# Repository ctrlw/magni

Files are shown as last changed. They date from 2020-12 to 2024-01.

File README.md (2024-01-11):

# magni
Buy me a coffee (https://www.buymeacoffee.com/ctrlw)

Software for a simple video magnifier running on Raspberry Pi. The first video demonstrates magnification and colour inversion, the second reading out text.

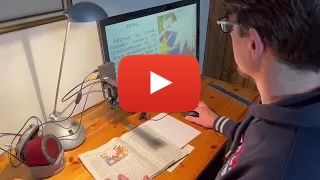
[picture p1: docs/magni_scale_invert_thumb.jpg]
Demo of video magnifier with magnification levels and colour inversion (https://youtu.be/32cXs6KolWk "DIY video magnifier demo scaling text and inverting colours")

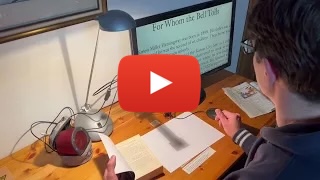
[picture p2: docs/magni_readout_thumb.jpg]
Demo of video magnifier reading out text from a book (https://youtu.be/zVkWfopQ86A "DIY video magnifier reading out text from a book")


## Description
This project aims to build a video magnifier based on Raspberry Pi and its camera. It can be used to see printed text or images at a larger scale, or to identify small parts like SMD electronics. The device has to be connected to a monitor which displays the magnified image from the camera. The user can step through predefined scale factors with a button or the Enter key, and step through different colour modes (like colour-inversion) with a second button or the "/" key. There's also basic support for reading out text (supports English, Spanish, French, German or Italian).

After the initial setup, the device works fully offline and does not need an internet connection.

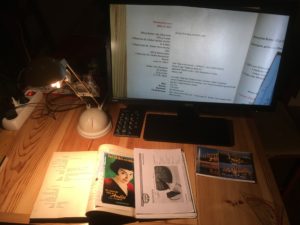
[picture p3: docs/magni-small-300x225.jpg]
Magnifier with low magnification

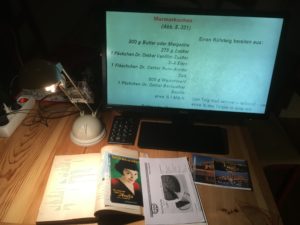
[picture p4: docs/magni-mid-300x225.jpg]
Magnifier with medium magnification

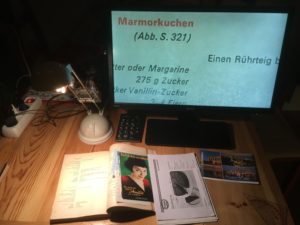
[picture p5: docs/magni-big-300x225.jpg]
Magnifier with high magnification


## Usage
The device boots directly into (slightly magnified) fullscreen camera view, which can take a minute depending on the Raspberry Pi model and SD card. It's important that the monitor is powered on at the same time as the Raspberry Pi or before, otherwise we may not get the full resolution. This can be achieved e.g. using a switchable socket or powering the Raspberry Pi directly from the monitor. 

The script supports multiple input sources:
* Mouse
  * Left button: switch to next magnification level (from smaller to bigger, then jump back to first)
  * Right button: switch between regular view and colour inversion / colour modes
  * Middle button: read out the text on the screen, stop it if already processing
  * Movement: no impact, the mouse is only used for its buttons. The recommendation is to prevent the mouse from accidental slipping, e.g. by sticking rubber bumpers on the bottom
* Keyboard (also supports a small numeric keyboard for the main features)
  * Enter: switch to next magnification level
  * /: switch between regular view and colour inversion / colour modes
  * r: read out the text on the screen, stop it if already processing
  * z: zoom in
  * Z: zoom out
  * a: autofocus (only with v3 camera, also happens automatically on each magnification change)
  * f: focus a bit closer
  * F: focus a bit further away
  * b: increase brightness
  * B: reduce brightness
  * c: increase contrast
  * C: reduce contrast
  * h: increase sharpness
  * H: reduce sharpness
  * t: increase saturation
  * T: reduce saturation
  * s: save the current preview as an image, name is the current timestamp
  * 1-0: set magnification level to specific value between 1 and 10
  * Esc or q: quit
* Push buttons via GPIO, one to iterate to the next scaling factor and one to switch between colour inversion / colour modes

## Hardware
To build the magnifier, you need at least the following
* Raspberry Pi
  * Any model you have will do (except Pi Pico), but if you're going to buy one I'd recommend the Pi 3 or Zero 2 W
  * Raspberry Pi Zeros are nice for their size, but need specific cables/adapters for camera and USB
  * Raspberry Pi 4 and 5 need specific cables/adapters and may also need cooling. They are overkill for the magnification task but could be faster for Text-To-Speech (reading out content)
* Raspberry Pi camera
  * Strongly recommended is an official Raspberry Pi camera v2 or v3, due to better image quality and flexible focus compared to the original 5MP ones. The v3 has autofocus which can be handy when supporting different distances to surface (e.g. when mounted on a flexible arm). However, the autofocus is not always accurate, so a v2 camera that is tuned to the right distance can be the better choice if you have a fixed distance to the surface. The high quality camera with additional lenses is not needed. The v3 version with Wide angle could be useful for close distances but has aberrations in the corners, so the regular v3 is probably the better choice.
* Raspberry Pi camera cable
  * only if the standard 15cm cable is too short or you need the smaller cable for Raspberry Pi Zero
* USB charger. For higher specced Raspberry Pi models (3 upwards) the official chargers are recommended due to better power stability
* Micro SD card (>= 4GB)
* HDMI monitor + cable. Some Raspberry Pi models work with analog TVs as well, but this hasn't been tested. A 22-24" FullHD monitor is good and can be found for 100
* Some input device. The easiest way is a USB (cable) mouse just for the buttons, but a numerical keyboard is also possible, or you can even solder physical push buttons to the GPIO
* Material for the mount

## Mount
The setup can be built in different ways, so let your creativity flow. Here are some examples:
* [Lamp setup](docs/magni-lamp-mount.md) (basic and simple)
* [Flexible arm](docs/magni-flexible-arm-mount.md) with one push-button
* [Box setup](docs/magni-box-mount.md) with 2 push-buttons
* [3d print for Pi Zero](docs/magni-3d-zero.md)

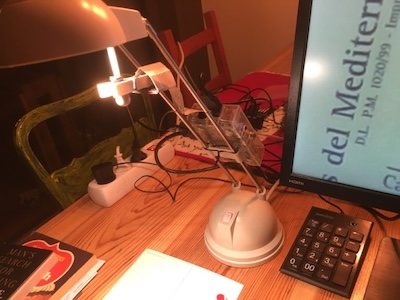
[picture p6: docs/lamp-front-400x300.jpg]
Simple lamp setup

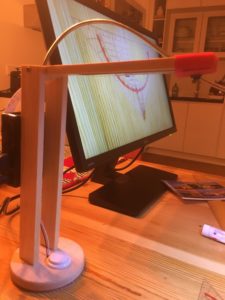
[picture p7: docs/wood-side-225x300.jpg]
Flexible wood arm

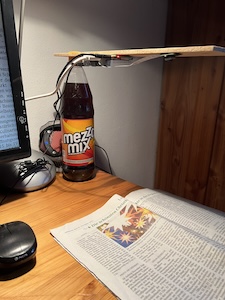
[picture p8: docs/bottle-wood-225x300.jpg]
Board on bottle

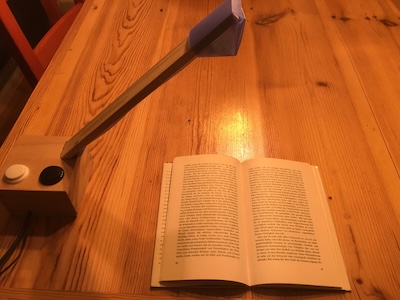
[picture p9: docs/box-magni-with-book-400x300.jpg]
Box setup with push buttons

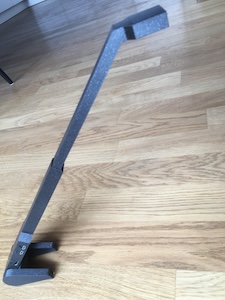
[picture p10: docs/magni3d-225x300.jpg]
3d print for Pi Zero

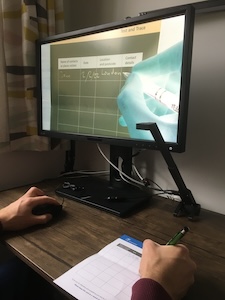
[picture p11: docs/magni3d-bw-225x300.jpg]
3d print for Pi Zero b/w

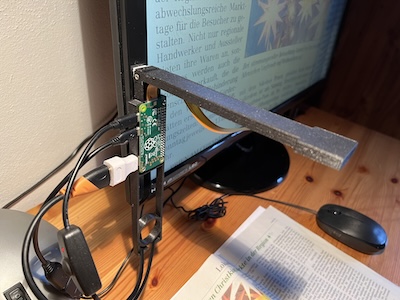
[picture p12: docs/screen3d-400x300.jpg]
3d print on monitor


A slightly more in-depth description of the first 2 hardware setups is given at http://www.fhack.org/2018/12/19/raspberry-pi-video-magnifier-2018/

If you use the optional push buttons instead of a USB mouse or numerical keyboard, the script expects them at GPIO 4 (physical 7) for the scale button and GPIO 18 (physical 12) for the colour button, using BCM numbering (4 being the 4th pin on the left, 18 being the 6th pin on the right of the GPIO). Each button needs to be connected with GND, e.g. at pins 9 and 14.
While physical buttons are nice, this involves soldering and they may be susceptible to electro-magnetic noise (e.g. getting triggered from switching some device on/off, or even from static charges from my Ikea Markus chair).

## Setup
**2021's Raspberry Pi OS "Bullseye" introduced some incompatible changes for the camera module. The following steps assume you use the latest OS, but the older "Bullseye" OS is still available as "Legacy OS" and allows to set the camera as Legacy camera in raspi-config (Interface options -> (Legacy) Camera -> Enable). The python script should work with both but the setup for legacy camera support is slightly different and can be found below.**
* Download [Raspberry Pi OS **Lite**](https://www.raspberrypi.org/software/operating-systems/) and install on SD card, e.g. with Raspberry Pi Imager. The 32 bit version is usually fine
* [Connect camera](https://www.raspberrypi.com/documentation/accessories/camera.html#connecting-the-camera)
* Login with default user “pi”, password “raspberry” (if on desktop, open a terminal). Using the default credentials is not secure, so change it if you will connect the device to the internet or have it accessible to strangers
* Run `sudo raspi-config`
  * System options -> Boot / Autologin -> Console Autologin
  * System options -> Wireless LAN (if you want to connect from another computer by wifi)
  * Interface options -> SSH -> Enable (only if you want to connect from another computer)
  * Finish and reboot (<Yes> or `sudo reboot`)
* Run the following commands in the terminal:
```
sudo apt update && sudo apt -y upgrade
sudo apt install -y python3-picamera2 python3-gpiozero python3-evdev python3-opencv
wget https://github.com/ctrlw/magni/raw/master/magni.py
chmod +x magni.py
echo "clear" >> .bashrc
echo "./magni.py" >> .bashrc
```
* To have a lower-quality fallback in case the monitor / TV is switched on *after* the magnifier, edit /boot/config.txt:
 `sudo nano /boot/config.txt`. This doesn't seem supported in the latest OS anymore.
  * Move to the line `#hdmi_force_hotplug=1` and delete the first character (#)
  * Leave nano with Ctrl-x, press “y” to save and enter to update the given file

* To hide the messages during startup, edit /boot/cmdline.txt:
`sudo nano /boot/cmdline.txt`
  * Append the following at the end of the line and save the file:
` logo.nologo quiet splash`
  * Leave nano with Ctrl-x, press “y” to save and enter to update the given file

### Legacy OS
The setup is the same as above with the following exceptions:
* In `sudo raspi-config` also enable Legacy camera support: Interface options -> Legacy Camera -> Yes
* When installing python libraries with apt, install `python3-picamera` instead of `python3-picamera2`, and you can skip `python3-opencv` as colour inversion is supported out of the box but not the colour modes
* For Readout (see below) use `bullseye` instead of `bookworm`. However, the area being read differs from the visible preview.
* You can use `libcamera-still` and `raspistill` instead of `libcamera-hello`

If you enable Legacy camera support, v3 cameras are not supported (at all, not just the autofocus!). The main advantage with legacy camera is the faster colour inversion, which can be otherwise slow on older models like the original Pi Zero or the Raspberry Pi models before the Pi 3. However, other colour modes like yellow on blue are only supported with the newer OS and needs opencv installed.

### Support reading out the visible text (OCR + TTS)
This feature is a very basic approach to read out text that is visible on the screen. It gets triggered when pressing the middle button of the mouse or "r" on an attached keyboard. Pressing the key again while it's still processing stops the background process.

All processing happens on the device itself (no internet needed), so better Raspberry Pi models will compute results faster. This feature is very sensitive to image quality and correct alignment, so ensuring good light, clear focus and horizontal text is necessary for reasonable results.

To make this work there are some extra dependencies. For Text to speech (TTS) we use pico2wave which is not included in the Raspberry Pi OS sources, so we have to add upstream Debian sources.
```
echo "deb [arch=armhf, trusted=yes] http://deb.debian.org/debian bookworm main contrib non-free" | sudo tee -a /etc/apt/sources.list
sudo apt update && sudo apt install -y tesseract-ocr libttspico-utils
wget https://github.com/ctrlw/magni/raw/master/plop.wav
```
The current OS (in late 2023) is based on bookworm. If you're on a different version you may have to adapt the first line accordingly, e.g. replace `bookworm` with `bullseye` if you're on the Legacy OS.

For other languages than English you need to install the related language packs. The used TTS package only supports 6 voices (en-GB, en-US, de-DE, es-ES, fr-FR, it-IT), so you can install all necessary OCR languages with
```
sudo apt install -y tesseract-ocr-deu tesseract-ocr-spa tesseract-ocr-fra tesseract-ocr-ita
```
and then update the language in magni.py, e.g.:
```
OCR_LANG = 'deu'   # Tesseract's character recognition: eng, deu, spa, fra, ita
TTS_LANG = 'de-DE' # Pico's Text to Speech: en-GB, en-US, de-DE, es-ES, fr-FR, it-IT
```

Sound may come through HDMI if you have a screen with speakers, or through the headphone jack of some models like the Pi 3. This can be changed in `sudo raspi-config` under System options -> Audio -> Headphones / HDMI. You can test that sound works running the built-in `speaker-test`.
There seems to be an issue where [audio via HDMI doesn't work as expected](https://forums.raspberrypi.com/viewtopic.php?t=351718). As a workaround you can force `aplay` to use HDMI output by uncommenting the second AUDIO line in the script to show `AUDIO = 'aplay -D sysdefault:CARD=vc4hdmi'` (if `speaker-test -D sysdefault:CARD=vc4hdmi` works).

### Support hard shut-down
This step allows to simply unplug the Raspberry Pi without possible damage to the SD card. This should be the last step in the setup, as the system will be made read-only (but it can be undone if needed).

Run `sudo raspi-config`
* Performance options -> Overlay File System
  * Enable overlay file system: Yes
  * Write-protect boot partition: Yes
  * Reboot? Yes

Now you can still create and modify files locally, but they will not be written to the SD card and disappear on the next reboot.
If you want to make the system writable again, you can do it in 2 steps with raspi-config:
* Disable the Overlay File System, so you can write to the file-system
* If you also want to modify the boot partition, you have to do it in a second step after rebooting

## Camera focus
**If you use the camera v3 with its autofocus you can skip this step as it doesn't need manual setup.**

When everything is in place, adjust the focus till a letter under the camera looks sharp. Then try a book and maybe adjust. Not all objects are flat. The  Raspberry Pi camera v2 usually comes with a white ring tool to easily adjust focus. On the older camera model or cheap alternatives, the lens may be glued and can still be adapted, but you risk breaking the camera.

You can do this with the magni.py script, or run `libcamera-hello --rotation 180 -t 0`:
* If you see the current camera view and it's at the same angle that you have from above (e.g. it’s not upside down), you’re good, otherwise try different values for rotation (0, 180) and adapt the ROTATION value in magni.py accordingly
* If the image is blurry you should adjust the focus, simply turning the lens with the plastic “wheel” that comes with the Pi camera v2
* Use Ctrl-c to get out of libcamera-hello (or Esc to leave the magni script)

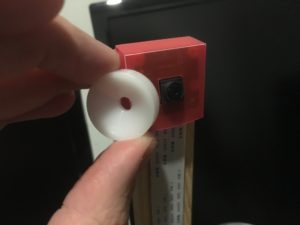
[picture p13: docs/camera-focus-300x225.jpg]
Adjust camera focus


## Modifications
You can easily adapt magni.py to your own setup and needs:
* `SCALE_FACTORS`: Modify this line to specify the scale factors
* `PIN_NUMBER_SCALE`: Set the (BCM) GPIO pin number where you connect the optional scale push-button
* `PIN_NUMBER_COLOR`: Set the (BCM) GPIO pin number where you connect the optional colour-mode push-button
* `ROTATION`: Change the value to the camera rotation in your setup if the camera is not placed behind the object (supports 0, 180; picamera on legacy OS also allowed 90 and 270 but this isn't the case on newer OS versions)
* `DISTANCE_TO_SURFACE_CM`: Can be overridden for v3 camera to fix the focus at a specific distance, default is autofocus
* `AUDIO`: Can be modified to force audio via HDMI if `raspi-config` isn't enough, just uncomment the respective line
* `BRIGHTNESS`: Can be modified to start with different brightness, values between -1.0 and 1.0
* `CONTRAST`: Can be modified to start with different contrast, values between 0.0 and 32.0
* `SHARPNESS`: Can be modified to start with different sharpness, values between 0.0 and 16.0
* `SATURATION`: Can be modified to start with different saturation, values between 0.0 and 32.0
* `COLOR_MODES`: Can be modified to change the list of supported colour modes to step through

## Limitations
* The monitor has to be switched on before or at the same time as the Raspberry Pi
* Magnification is done in software, so scale factors of 10 and above tend to be noisy
* On older cameras the camera focus is fixed, so it cannot adapt to objects that are much closer or further away. Pi camera v3 supports autofocus but it's often not that accurate
* It may take a minute from power on till the picture is shown (depending on model and SD card)
* The readout feature is very basic and mostly a proof of concept

## Alternatives
This is a fun project, but also consider these alternatives to building your own video magnifier
* Smartphones and tablets usually come with a magnification option, e.g. the built-in [Magnifier on iOS](https://support.apple.com/en-us/HT209517) and [Google's Magnifier on Android](https://play.google.com/store/apps/details?id=com.google.android.apps.accessibility.magnifier)
* A mounted magnifying glass as they are used in nail salons
* Professional video magnifiers are optimised for low vision users with varying needs and conditions. While they cost in the thousands, it's often possible to find them much cheaper used, e.g. on Ebay. Depending on your location, health insurance providers or organisations for the Blind may also have special offers or even provide support for free
* Others have come up with similar DIY solutions which may be better suited, e.g.
  * [Precision zoom on Raspberry Pi](https://www.instructables.com/Raspberry-Pi-Zero-HDMIWiFi-Soldering-Microscope/)
  * [Borescope camera and laptop](https://www.instructables.com/Reading-Aid-for-the-Partially-Sighted/)
  * [USB camera and laptop](https://github.com/mikeh69/EVidMag)

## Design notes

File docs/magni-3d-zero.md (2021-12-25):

# Small 3d printed video magnifier
Simple and compact 3d-printed setup that is good enough for books and also works for the occasional letter. For Raspberry Pi Zero with 30cm ribbon cable. Uses mouse buttons for input.

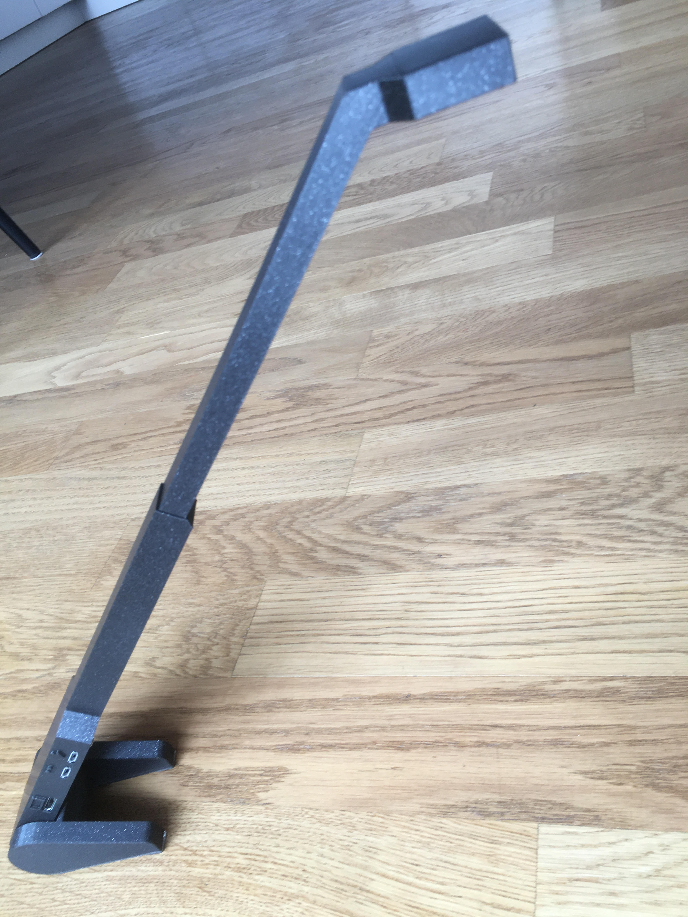
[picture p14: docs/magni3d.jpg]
Assembled magni


## Ingredients
* HDMI monitor (22-24 inch is a good size)
* Raspberry Pi Zero
* Raspberry Pi Camera v2
* 30cm camera ribbon cable for Raspberry Pi Zero
* USB Mouse (as input device)
* Micro USB to USB adapter (for the mouse)
* 8 screws (2mm diameter, 10mm length)
* 1 M16 connecting nut (16mm screw diameter, 24mm outer diameter, 50mm length) as weight
* HDMI cable with one side mini HDMI, other normal size HDMI
* Micro USB charger
* (optional) rubber stickers to stick under the mouse, to avoid it moving (as we only use the buttons)

## 3d printed parts
Print the following parts on a 3d printer (tested with PLA on a Prusa Mini):
* [Body](../stl/zero-wide-body7.stl)
* [Cover for body](../stl/zero-wide-bottom7.stl)
* [Camera arm](../stl/zero-wide-arm3.stl)
* [Cover for arm](../stl/zero-wide-arm3-inner.stl)
* [Foot](../stl/zero-wide-foot7.stl)
* [Other Foot (same file, but you have to flip it before printing)](../stl/zero-wide-foot7.stl)

## Building
* Attach camera cable to camera, pass the cable through the camera arm and screw the cover onto the camera
* Stick camera arm into body
* Attach other end of the camera cable to Raspberry Pi
* Screw the body cover onto Raspberry Pi
* Insert M16 nut into the cavity at the end of the body
* Stick feet on both sides of the M16 nut so the device is at a 45 degrees angle
* Connect HDMI cable to the monitor
* Connect mouse and micro USB adapter to the center micro USB port
* Connect micro USB charger to the other micro USB port

## Usage
One mouse button iterates through the pre-defined magnification factors, the other switches between normal and inverted colour mode.
Smaller items like books can be moved under the device. For bigger items like newspapers the device has to be moved on top of the paper which is less convenient.

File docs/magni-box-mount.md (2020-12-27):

# Box mount video magnifier
This setup uses a square box with a diagonal camera arm. Box and arm can be laser-cut, while you may want to 3d-print the camera enclosure or build it from plastic. If you position the magnifier on the side and not behind the object, you also have to adapt the ROTATION in the magni.py script. Image quality is worse when positioned sideways (with rotation 90 or 270).

This is more of a prototype that someone might want to expand on.

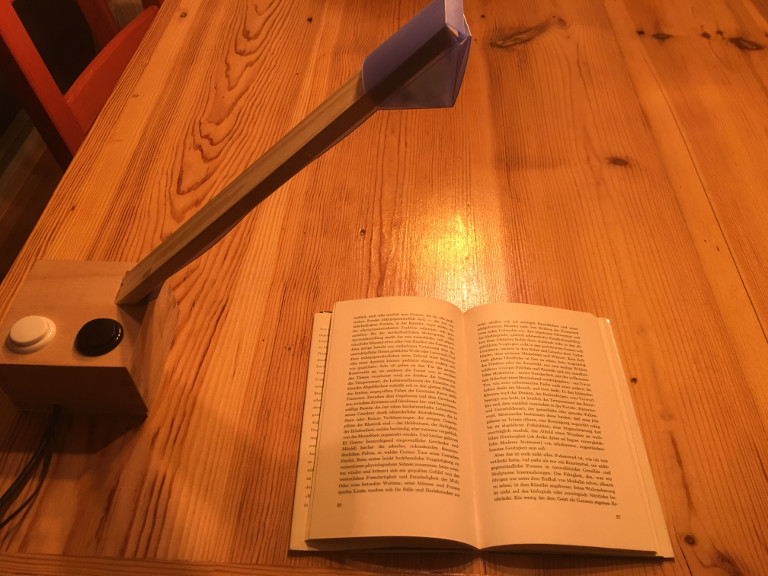
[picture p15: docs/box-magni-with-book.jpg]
Magni sideways


## Ingredients
* 2 Push-buttons (3cm diameter) and cables (like this [arcade set](https://www.amazon.de/dp/B06XDG6PC1))
* Wood glue
* ~A3 sized ply wood (4mm thick, laser-cuttable)
* Access to a laser-cutter
* LED lamp (optional, not shown here)

## Building
Cut the wood according to this [SVG for laser-cutter box](box-magni-laser-4mm.svg). Red lines should be cut, green just marked and blue can be carved for cables to add an LED light. The design hasn't taken into account that laser cuts also have a width, so the parts will not be stable just by combining them, but the wood needs to be glued.
For illustration purpose here's an older [pdf for laser-cutter box](box-magni-laser-a4.pdf), which does not contain the camera arm and may not be adapted to 4mm wood.

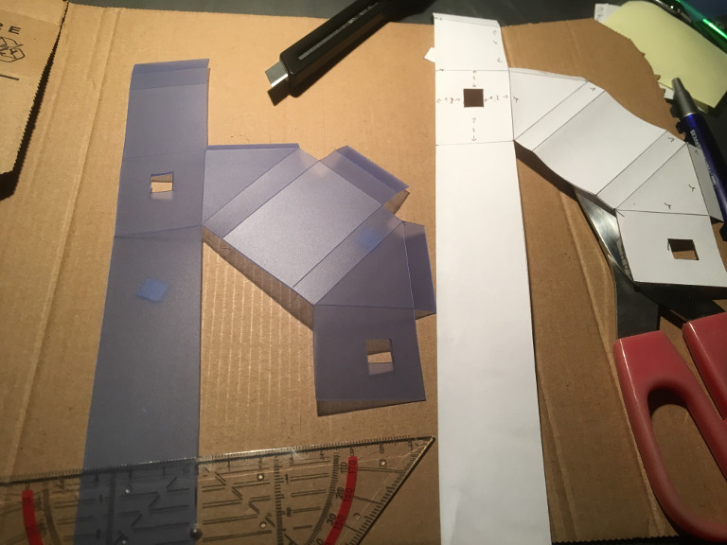
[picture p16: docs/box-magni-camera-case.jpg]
Camera enclosing


## Usage
One push-button steps through magnification levels, the other toggles colour inversion.

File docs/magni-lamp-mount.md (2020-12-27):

# Lamp mount video magnifier
This is the most basic setup. 

## Ingredients
* Raspberry Pi case (had a Raspberry Pi 1 with official case)
* Lamp (had a basic halogen lamp from the hardware store)
* Numeric keypad
* Wooden peg with a bit of rubber gum inside
* Twist tie (to attach the case to the lamp)
* Cardboard to “protect” the camera

## Building
There’s really nothing to it. Very simple to “build”. Not exactly stable.

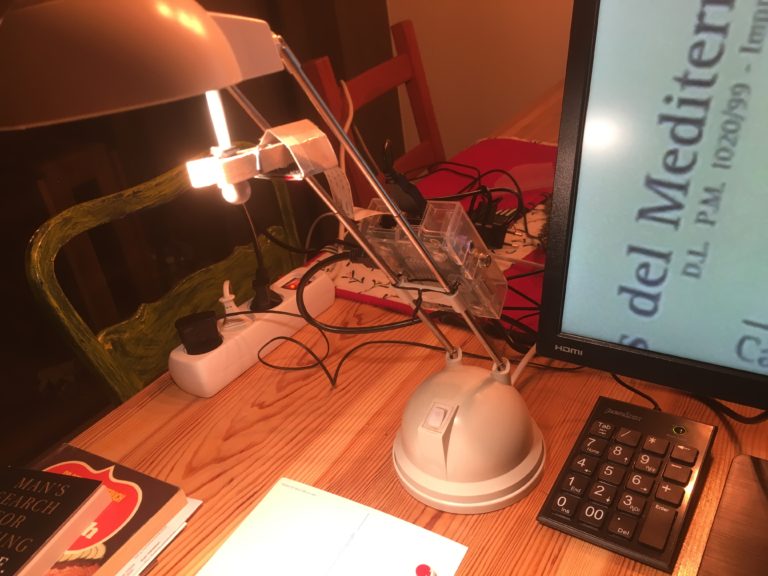
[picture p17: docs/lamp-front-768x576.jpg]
Magni lamp setup front

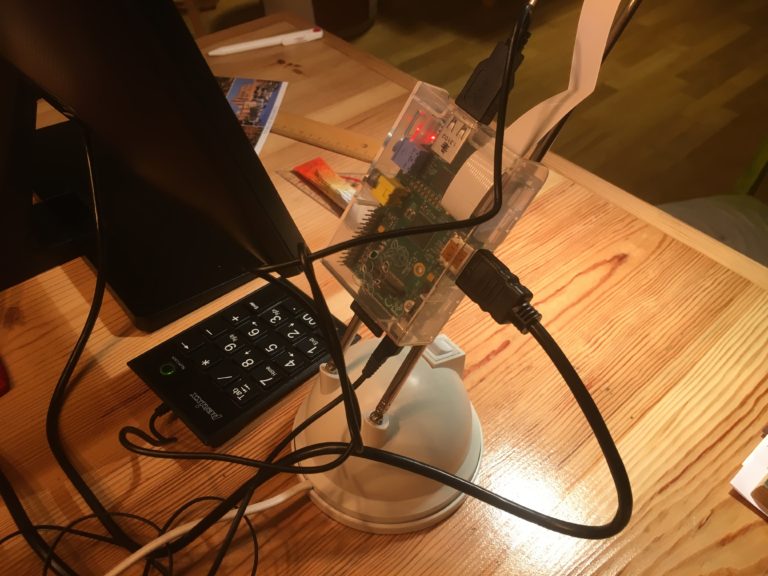
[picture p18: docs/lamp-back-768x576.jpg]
Magni lamp setup back


## Usage
Pressing a digit on the numeric keypad switches magnification to that factor (except for too small values, i.e. "1" normally does nothing). Pressing the Enter key switches to next preset magnification level. Pressing “/” inverts colours (some people are better reading white text on black background). This is not exclusive to this build, of course the keypad can also be attached to other versions.

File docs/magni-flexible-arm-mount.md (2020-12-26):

# Flexible arm magnifier
This design is more (wood-) work. The arm is flexible, so the device can be folded for transport. The single button makes it easy to use, and you can move the arm up and down to see more / less (e.g. slightly move upwards for a big newspaper). Sizes can be adapted for its typical use case, e.g. for regular newspaper reading a bigger stand may be needed. 

Flexible arm magnifier setup

## Ingredients
* Raspberry Pi case with holes for GPIO cables
* USB LED lamp
* Wood (3cm x 1cm, 2 * 25cm, 1 * 20cm)
* Wooden wheel (10cm diameter, 1.5cm thick or more)
* Screws (4 * 2 cm to fix arm and Raspberry Pi, 2 * 4cm to fix bottom)
* Flex band 30cm for Raspberry Pi camera (or 50 cm if you make it bigger)
* Plastic to fold the camera case
* 2 jumper cables, 1 resistor (used 1k Ohm)
* 1 push button (3cm, taken from arcade joystick set)
* Rubber to keep it in place and protect push button electronics
* Tools: saw (Japan saws are great!), 2-3mm drill for pre-drilling the screws, 3cm drill for drilling the button hole, screwdriver, soldering equipment, cardboard cutter, glue

## Build
Below is a kind of step-by-step photo story. The screws for the case are about 15cm above the top of the base.

The jumper cables are attached to GPIO 7 and 9, i.e. the 4th pin on the left side and the neighbouring GND. I had to bend the push button connectors and break off one of its plastic pieces. Also cut one side of the jumper cables to solder to the button / resistor.

For the push-button I mostly followed https://raspberrypihq.com/use-a-push-button-with-raspberry-pi-gpio, and avoiding multiple click events with bounce time was a helpful addition from https://www.raspberrypi.org/forums/viewtopic.php?t=146369

The “case” for the camera is cut and glued from plastic and about 3cm x 3cm, with a height of 1.3cm, basically the wood plus about 3mm. The camera lens watches through an 8mm square. You can also 3d-print the [camera case STL](./magnicam.stl)

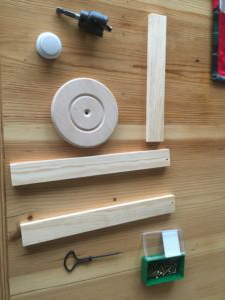
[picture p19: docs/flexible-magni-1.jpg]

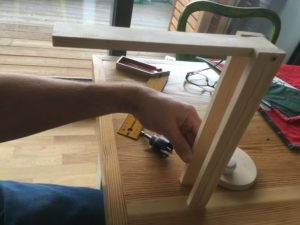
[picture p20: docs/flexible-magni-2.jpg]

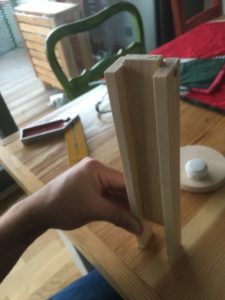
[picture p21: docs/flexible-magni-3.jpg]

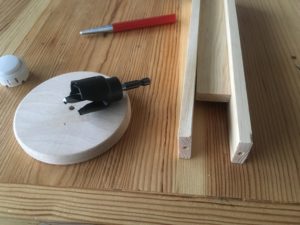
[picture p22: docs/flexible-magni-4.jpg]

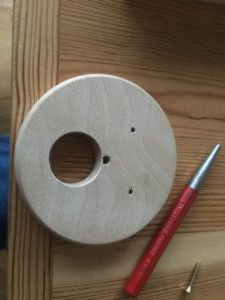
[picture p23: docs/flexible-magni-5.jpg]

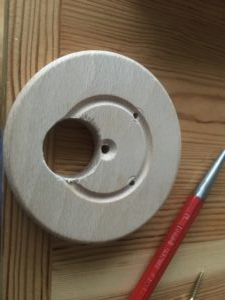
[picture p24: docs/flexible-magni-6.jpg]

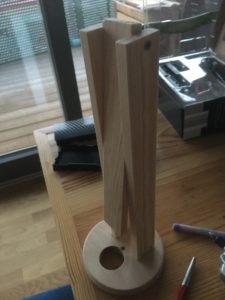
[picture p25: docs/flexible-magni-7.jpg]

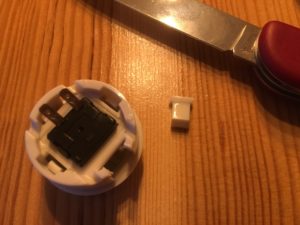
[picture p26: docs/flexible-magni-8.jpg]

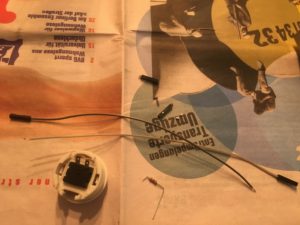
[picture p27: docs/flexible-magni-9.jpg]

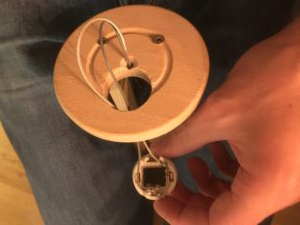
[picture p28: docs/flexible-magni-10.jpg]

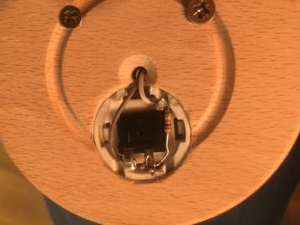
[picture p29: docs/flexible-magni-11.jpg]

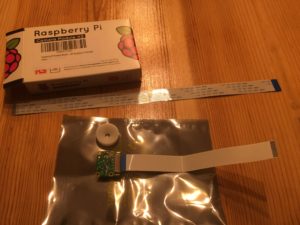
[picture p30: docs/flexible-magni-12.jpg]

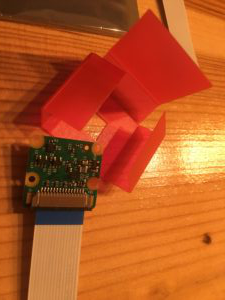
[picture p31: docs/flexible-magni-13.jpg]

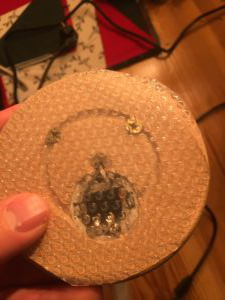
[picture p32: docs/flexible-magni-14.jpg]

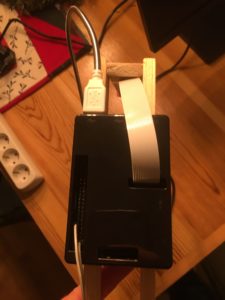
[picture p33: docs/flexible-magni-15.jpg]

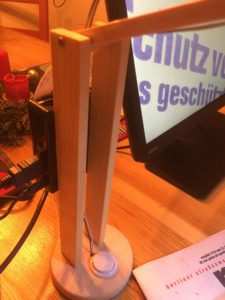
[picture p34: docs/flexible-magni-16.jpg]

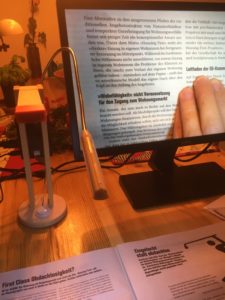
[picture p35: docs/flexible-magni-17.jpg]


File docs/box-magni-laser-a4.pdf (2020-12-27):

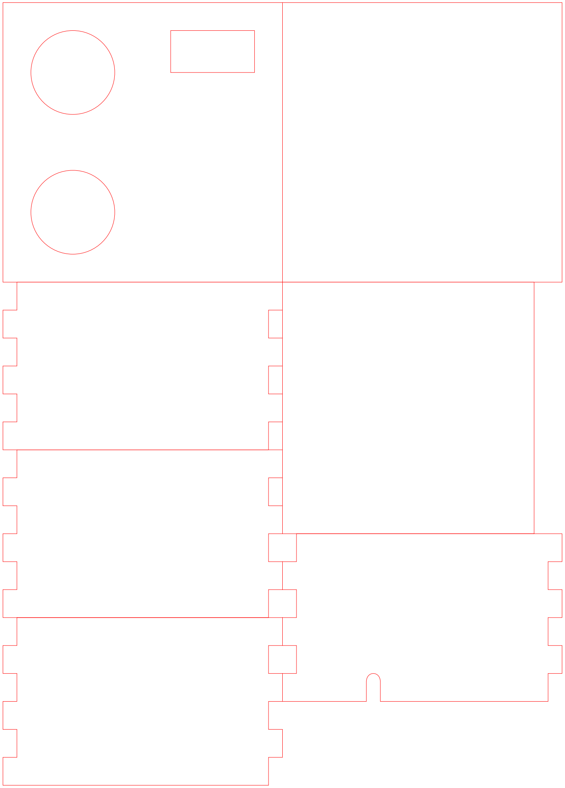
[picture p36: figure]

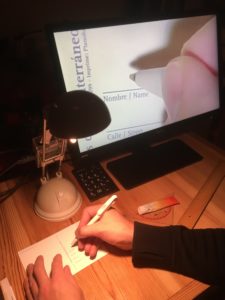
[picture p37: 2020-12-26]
docs/form-225x300.jpg

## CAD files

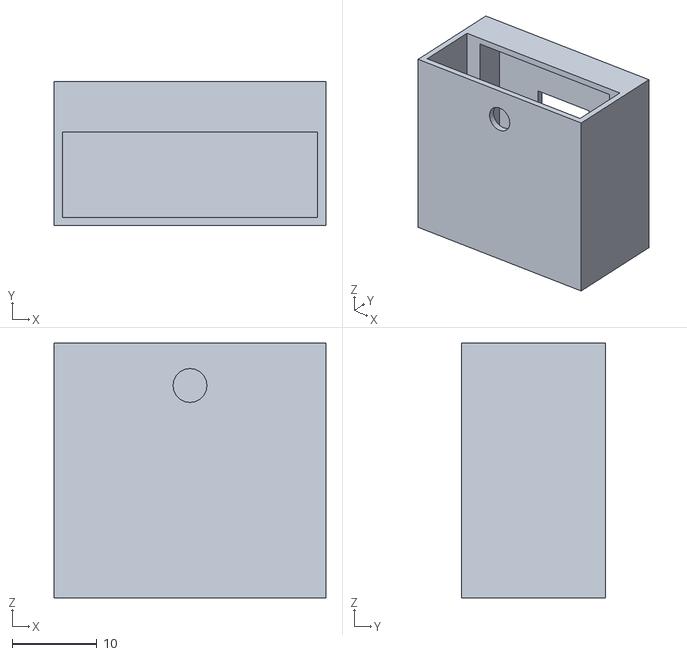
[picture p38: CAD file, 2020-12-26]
docs/magnicam.stl
32.0 x 17.0 x 30.0

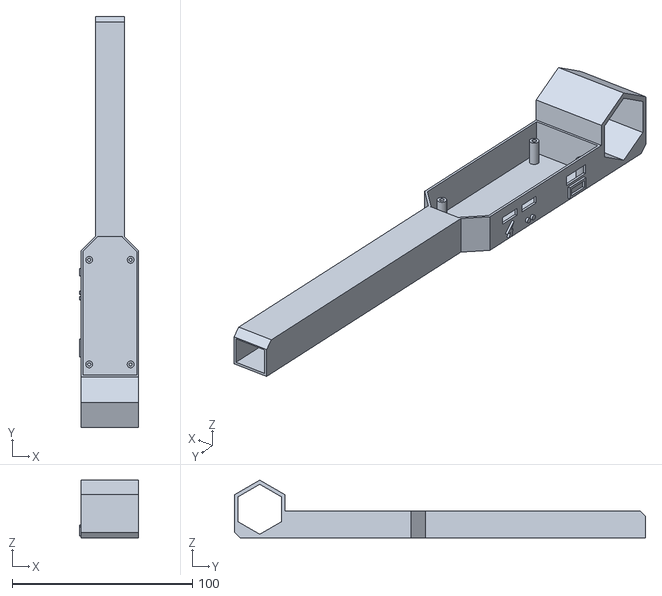
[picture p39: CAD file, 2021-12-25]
stl/zero-wide-body7.stl
33.0 x 228.0 x 32.0

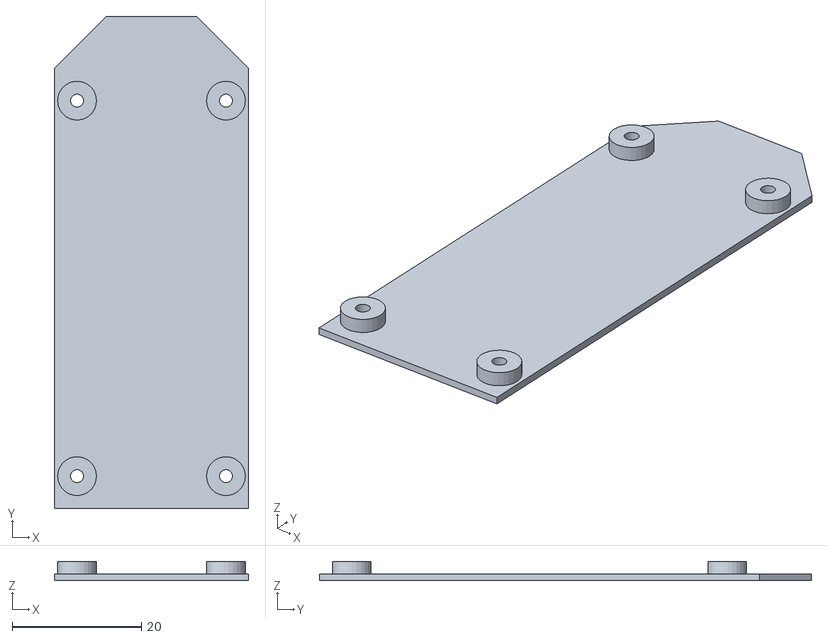
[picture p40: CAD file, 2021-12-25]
stl/zero-wide-bottom7.stl
30.0 x 76.0 x 3.00

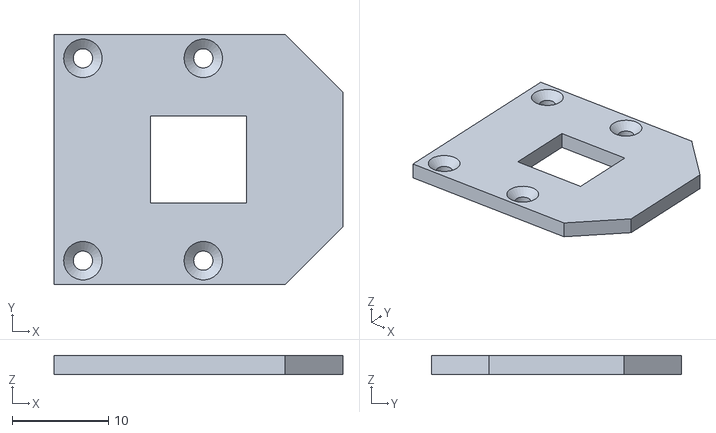
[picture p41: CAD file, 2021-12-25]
stl/zero-wide-arm3-inner.stl
30.0 x 26.0 x 2.00

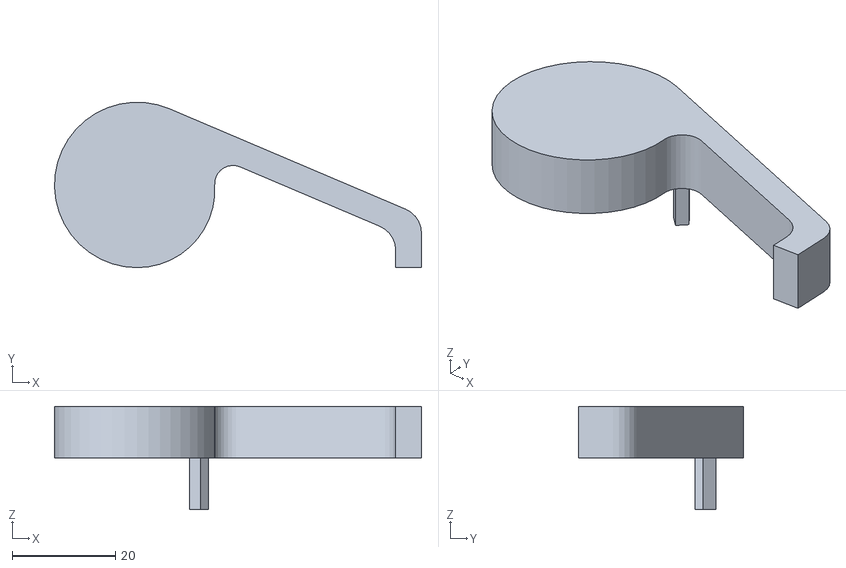
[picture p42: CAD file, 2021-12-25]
stl/zero-wide-foot7.stl
71.0 x 32.0 x 20.0

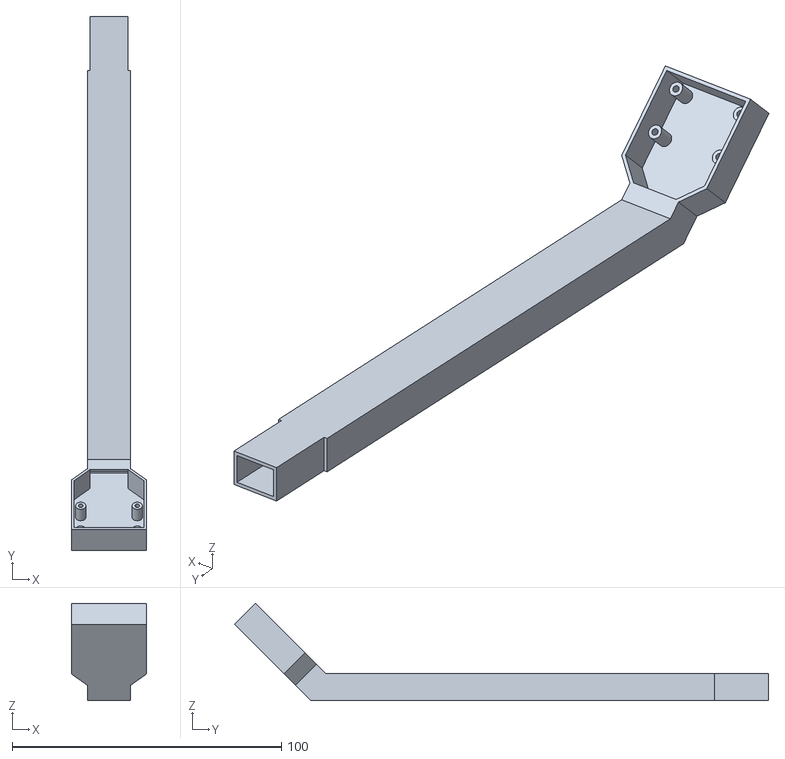
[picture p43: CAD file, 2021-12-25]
stl/zero-wide-arm3.stl
28.0 x 198.3 x 36.1

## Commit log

2019-03-15 fixed pin name
2020-12-25 Updated README.md for Raspberry Pi OS and PiCamera changes
2020-12-26 Add 2 build setups to documentation (lamp and flexible arm)
    [magnicam.stl]
2020-12-27 Description for 3rd housing with laser-cut box
2021-12-25 Add steps for new Raspberry Pi OS "Bullseye"
    Raspberry Pi OS Bullseye from November 2021 broke camera compatibility.
    Updated steps in description.
    https://www.raspberrypi.com/documentation/accessories/camera.html#libcamera-and-the-legacy-raspicam-camera-stack
2021-12-25 Description for 3d printed magni
    [zero-wide-arm3-inner.stl, zero-wide-arm3.stl, zero-wide-body7.stl, zero-wide-bottom7.stl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]
2023-12-06 Support new OS and autofocus
    Major update that adds
    * picamera2 support (for newer OS like Bullseye, Bookworm)
    * Still supports legacy OS with picamera
    * Pi Camera 3 autofocus on each magnification change (button press)
    * Supported only on new OS, not legacy
    * No continuous autofocus as it was too noisy
    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
2023-12-07 Update Readme to cover the latest OS and v3 camera
    Removed outdated info for legacy OS that doesn't apply to current OS Bookworm
2023-12-19 Support reading out the text in preview when pressing "r"
    Pressing "r" during readout processing stops it
    readout() saves the current preview as .jpg, performs OCR and TTS, then plays the resulting .wav
    Everything is performed offline on device, no internet needed
    Tesseract is used for optical character recognition (OCR)
    Pico is used to convert the analysed text to a wave file
    The .wav is played with aplay
    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
2023-12-20 Update documentation for Legacy OS + Legacy camera support
2023-12-20 fix: fix autofocus for v3 camera, add optional fixed focus
2024-01-03 feat: workaround for HDMI sound output
    Added an alternative if setting the sound output to HDMI in `raspi-config` does not work
    See https://forums.raspberrypi.com/viewtopic.php?t=351718
2024-01-04 feat: add text overlay for debug info, disabled by default
    Displays the current zoom factor if enabled
    The text is ugly and in the way, so by default not enabled
    To work it needs numpy and opencv installed
2024-01-04 feat: add manual focus on f and F keys, autofocus now on a
    Only for supported cameras like the v3 camera
    Pressing 'a' now triggers autofocus (used to be 'f')
    Pressing 'f' now moves the focus closer, 'F' further away
    Autofocus for the preview area is still triggered on each magnification change
2024-01-10 minor: use ScalerCropMaximum instead of PixelArraySize
    ScalerCropMaximum should be cleaner as it gives the maximum rectangle of the current camera configuration
    No visible impact by this code change
